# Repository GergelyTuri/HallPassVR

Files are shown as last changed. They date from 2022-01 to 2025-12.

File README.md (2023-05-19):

# HallPassVR
## Virtual reality system for head-fixed mouse experiments. 

See published paper on [JOVE](https://app.jove.com/v/64863/an-open-source-virtual-reality-system-for-the-measurement-of-spatial-learning-in-head-restrained-mice).

We developed an inexpensive, single board computer-based, easy-to-use setup for investigation of mouse spatial learning behavior using a visual virtual reality (VR) environment. This system uses a network of microcontrollers (ESP32) and a Raspberry Pi single-board computer to display a virtual linear track to a headfixed mouse running on a wheel. Along with a custom software package written in Python and C++ to generate parameterized virtual environments, this methodology allows researchers the design of various spatial navigation-based experiments to study neural circuits in the brain underlying spatial behaviors. [Example video here](https://www.youtube.com/watch?v=iCfhJT3dYIo):  

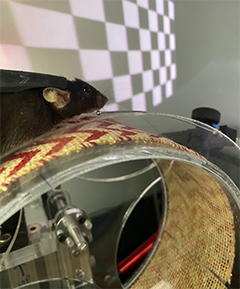
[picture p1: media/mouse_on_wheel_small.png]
Mouse on wheel


## Main hardware requirements: 
1. _ESP32 microcontrollers_ to track and convert mouse movement on a treadmill or wheel to serial data and to control other harware elements (lick spout for reward delivery).
2. _Raspberry Pi 4_ for building and simulating the virtual reality environment. 
3. _Projector_ for visualizing the virtual corridor.
4. PCB shields through [OpenMaze](https://claylacefield.wixsite.com/openmazehome/openmaze-shields)

## Software requirements: 
1. The virtual corridor was designed with _Python_. 
2. Native, Linux-based OS for Raspberry Pi.
3. _tkinter_ was used for designing the graphical user interface.
4. _Arduino IDE_ for programing the microcontrollers.
5. _Processing_ for data collection and plotting.
6. The analysis of behavior files currently requires _Matlab_.

### What we have done: 
1. We built the main part of the system which can simultaneously run and show the virtual reality environment on a computer display and a projector.
2. We have built a prototype GUI which can be used to build virtual corridors from virtually any kind of jpeg images.
3. We tested the system with several testbenches.

### Work in progress: 
1. Finalizing the code by adding documentation and examples.
                
### Future plans: 
1. Optimization of the system by e.g., adding an RFID sensor to increase wheel tracking accuracy.
3. Adding other features to the VR software like naturalistic scenes, looming stimulus or cliff-like effects. 
4. Implementing the analysis scripts in Python.
5. Increasing the flexibility of the existing protocols. 
6. Implementing a wireless (e.g., bluetooth) system using this platform.
## Quickstart:
### Initializing VR environment: 

1. Open a terminal window in Raspberry Pi and navigate to the `HallPassVR` folder
 ```bash
cd /home/pi/Documents/HallPassVR
 ```
2. Starting the VR GUI:
```bash
python3 HallPassVR_GUI.py
 ```
3. Setting up the floors and corridors in the GUI
4. Setting up `Processing` sketch to acquire and plot behavior.
5. Preliminary analysis of the acquired data can be done in Matlab with the scripts in `/Analysis code` folder.

#### GUI: 
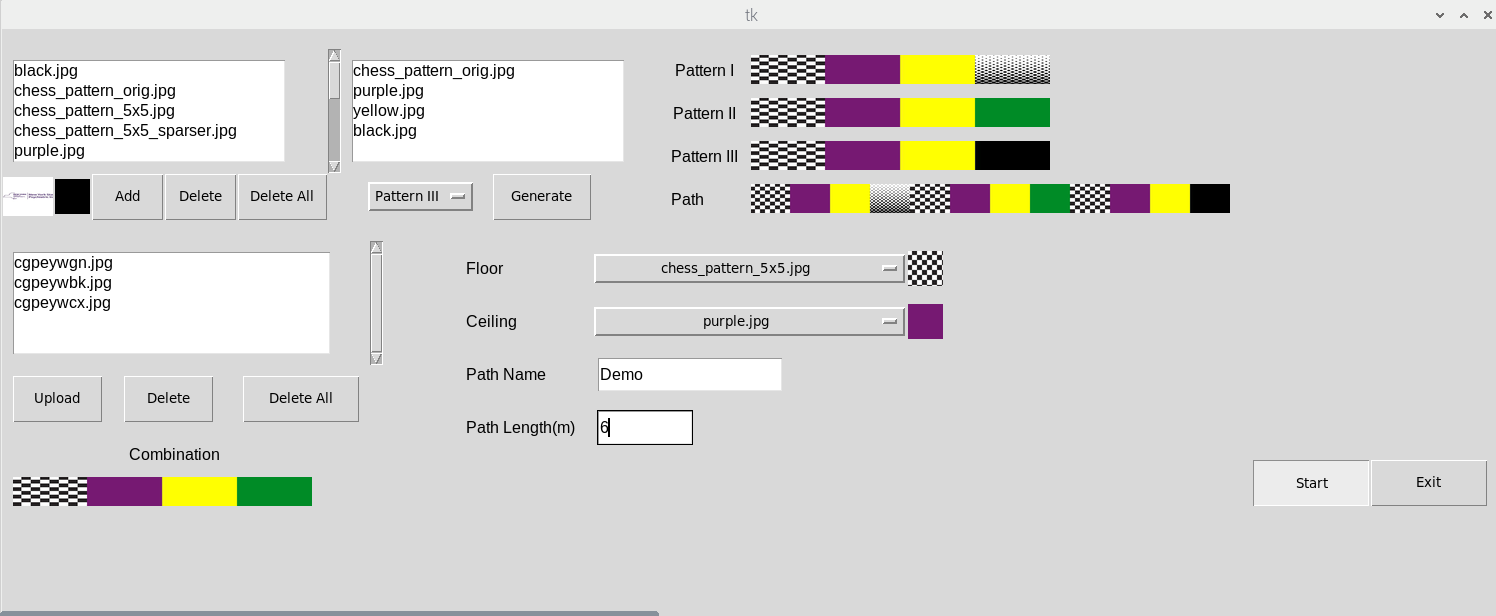
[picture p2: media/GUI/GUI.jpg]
GUI


#### Example virtual corridor: 
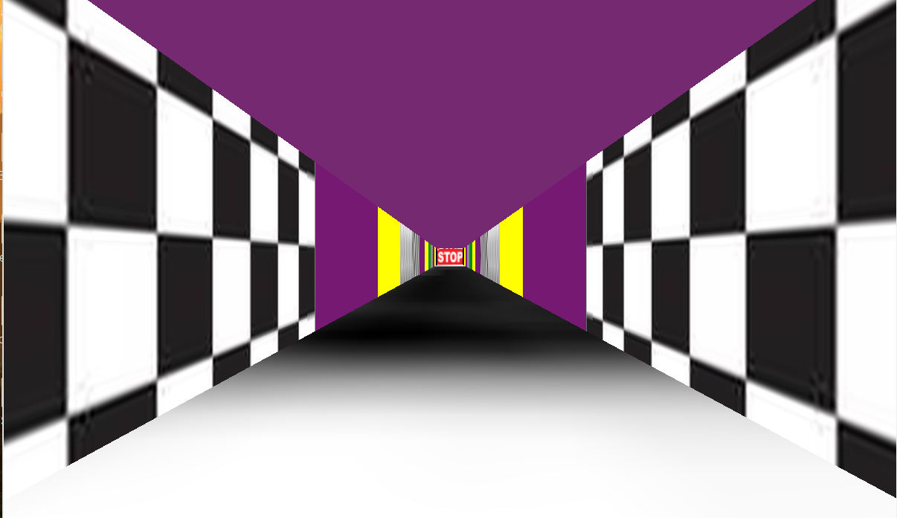
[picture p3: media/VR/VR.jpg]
corridor


For feature requests, support or questions, please open a ticket on [GitHub](https://github.com/GergelyTuri/mouseVR/issues).

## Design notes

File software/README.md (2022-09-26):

# HallPassVR software
## Virtual reality system for head-fixed mouse experiments. 

## Arduino code
1. Rotary encoder ESP32
2. Behavior ESP32 (with OMwESP32 PCB shield)

## Analysis code
MATLAB code for analysis of spatial licking behavior using .txt file output from Processing behavioral acquisition.

## Processing code
Code in the Processing.org environment to acquire data from behavior ESP32 during HallPassVR and plot relevant online behavioral events (and animal motion along the virtual linear track).

## HallPassVR Python code
To be copied onto RaspberryPi to run HallPassVR virtual linear track environment and GUI.

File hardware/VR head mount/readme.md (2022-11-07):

# This folder contains assembly files and instructions for the head mounting apparatus. 

Our headpost design consists of two interlocking manifolds for securing a metal headpost. We used a high resolution tabletop SLM 3D printer to manufacture the holding arms. The resin printed plastic is able to provide stable head fixation for behavior experiments, however, to achieve maximum stability for sensitive applications like single cell recording or two-photon imaging, we recommend using machined metal parts. The headpost holder is installed on two goniometers, with the tilting axes positioned perpendicular to each other, thus the animal’s head can be tilted to 4 directions after head fixation to level the preparation. The goniometers can represent a large price tag in this build, however, this feature is indispensable for chronic in vivo imaging experiments when finding the same cell population on subsequent imaging sessions is required. We deposited two types of head posts with different complexity (and price) we regularly use in our labs. Depending on the experiment type, the user should decide which one to implement. The head bars are made of steel (e.g., Stainless 304 Annealed) and we generally outsource the manufacturing of these parts to our local machine shop or to an online service (e.g., eMachineShop).

| material | description | source |
| -------- | ----------- | ------ |
| head post holder | custom 3D print | |
|set screws| M2.5 x 6 | McMasterr Carr|
|thumb screws|8-32 x 1/2"| McMasterr Carr|
|goniometers| Edmund Optics | 66-526, 66-527 |
| metal headposts | Stainless 304 Annealed or Titanium| [eMachineShop](https://www.emachineshop.com/)|
| optical posts (2) | 1/2" series| Thorlabs|
|right angle clamp| RA90| Thorlabs|

### Final look:
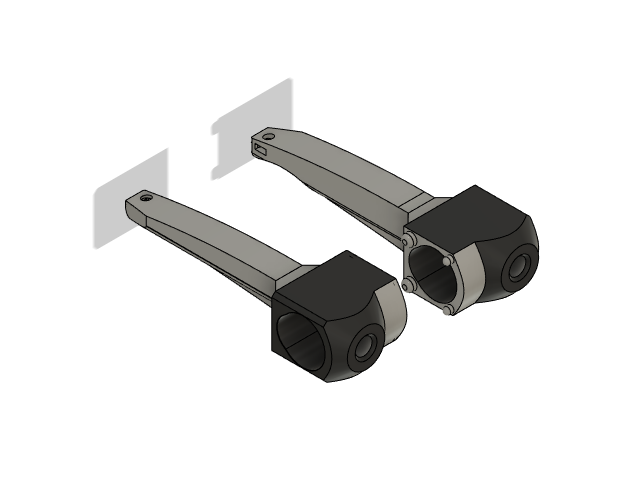
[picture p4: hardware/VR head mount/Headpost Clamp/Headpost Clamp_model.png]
clamp


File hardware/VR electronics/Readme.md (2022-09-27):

# Instructions for the electronic components

Files in the `ESP32 files` directory should be uploaded to the ESP32 boards connected to the lickport and rotary encoder. 

Files in `/PCBs` can get manufatured with companies specialized to PCB production. Typically we use [OSH Park](https://oshpark.com/) if we don't want to modify the design. More info on how to order and assemble these shields can be found on [OpenMaze](http://www.openmaze.org/).

| material | description | source |
| -------- | ----------- | ------ |
| Raspberry Pi 4 model B | single-board computer | e.g., raspberrypi.com, adafruit.com |
| rotary encoder | ENS1J-B28-L00256L | digikey.com[^1] |
|ESP32 devKitC v4 | microcontroller (x2)| e.g., [Amazon.com](https://www.amazon.com/s?k=ESP32&crid=ZCZ3J597DJO9&sprefix=esp32%2Caps%2C94&ref=nb_sb_noss_1)|
|OpenMaze OMwESP32 shield| custom design | see: `/PCBs` folder |

[^1]: Alternative sources: amazon.com, mouser.com, DigiPart, etc.

## Installation instructions for Raspberry Pi:
### Configure RaspberryPi 4 model B 
This single-board computer has an onboard GPU to facilitate VR environment rendering, as well as two HDMI ports for experiment control/monitoring and VR projection.
1. Download Raspberry Pi Imager app and install OS (currently RaspberryPi OS r.2021-05-07) on microSD card (8GB+), insert and boot Raspberry Pi.
2. Configure Raspberry Pi: (menu bar) 
- `Preferences>Raspberry Pi Configuration>`
  - `Display>Screen Blanking>Disable`
  - `Interfaces>Serial Port>Enable` 
  - `Performance>GPU Memory>256`
3. In the terminal: 
``` bash
sudo nano /boot/config.txt
``` 
then uncomment `config_hdmi_boost=4`. Save, reboot the Raspberry Pi.

4. Download and install Arduino IDE from arduino.cc/en/software (e.g. arduino-1.8.19-linuxarm.tar.gz)
5. Download and install Processing IDE from github.com/processing/processing4/releases (e.g. processing-4.0.1-linux-arm32.tgz)
6. In the terminal
```bash
sudo pip3 install pillow –-upgrade
```
7. Then, 
```bash
sudo pip3 install pi3d
```
8. Install ESP32 support on Arduino IDE.

## Set up rotary encoder-ESP32 connections
1. Connect wires between rotary encoder and ESP32.
2. Connect serial RX/TX wires between ESP32 Serial2 (pins 16,17) and behavior ESP32.
3. Connect serial RX/TX wires between ESP32 Serial0 (RX/TX) and Raspberry Pi GPIO (or direct USB connection).
4. Set up behavior ESP32 connections with behavioral hardware (via OMwESP32small PCB).
5. Connect 12V liquid solenoid valve to ULN2803 IC output (e.g. pin#32).
6. Connect lick port to ESP32 touch inputs (e.g. T2, GPIO15).
7. Connect serial RX/TX wires between behav ESP32 Serial2 (pins 16,17) and rotary encoder ESP32 (see above #1.b.).
8. Plug USB into Raspberry Pi USB port (or other PC running Processing to capture behavior data).
9. Plug Raspberry Pi HDMI #2 output into projector HDMI port.

## Set up software (rotary encoder ESP32 and behavior ESP32 w. OM PCB)
1. Plug rotary encoder ESP32 into Raspberry Pi USB port first- it will be automatically be named `/dev/ttyUSB0`
2. Load rotary encoder arduino code by first selecting the ESP32 under `Arduino IDE>Tools>Boards>ESP32 Dev Module`, then `Tools>Port`>`/dev/ttyUSB0`, then click `Upload`: `RotaryEncoder_Esp32_VR.ino`
3. Plug behavior ESP32 into Raspberry Pi USB port next- it will be named `/dev/ttyUSB1`
4. Load behavior sequence arduino code (ESP32 Dev Module already selected), then `Tools>Port>` `/dev/ttyUSB1`, then click `Upload`: `wheel_VR_behavior.ino`
5. You can test serial connections by selecting the Port in the Arduino IDE, then clicking on `Tools>Serial Monitor` (baud rate:115200), to observe serial output from the rotary board (USB0) or the behavior board (USB1).
6. Download HallPassVR python code from this GitHub repo (`/software/HallPassVR`) to `/home/pi/Documents`.

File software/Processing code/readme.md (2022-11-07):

# HallPassVR
## Virtual reality system for head-fixed mouse experiments. 

Processing code to record and graph serial data from behavior ESP32 (w. HallPassVR).

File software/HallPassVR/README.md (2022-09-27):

# HallPassVR
## Virtual reality system for head-fixed mouse experiments. 

To be copied onto RaspberryPi to run HallPassVR virtual linear track environment and GUI.

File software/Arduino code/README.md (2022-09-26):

# HallPassVR
## Virtual reality system for head-fixed mouse experiments. 

Code written for Arduino IDE to run rotary encoder ESP32 and behavior ESP32 with OpenMaze OMwESP32 PCB.

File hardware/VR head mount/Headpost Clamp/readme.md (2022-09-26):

### This folder contains assembly files and instructions for the headpost holder. 

#### Design:

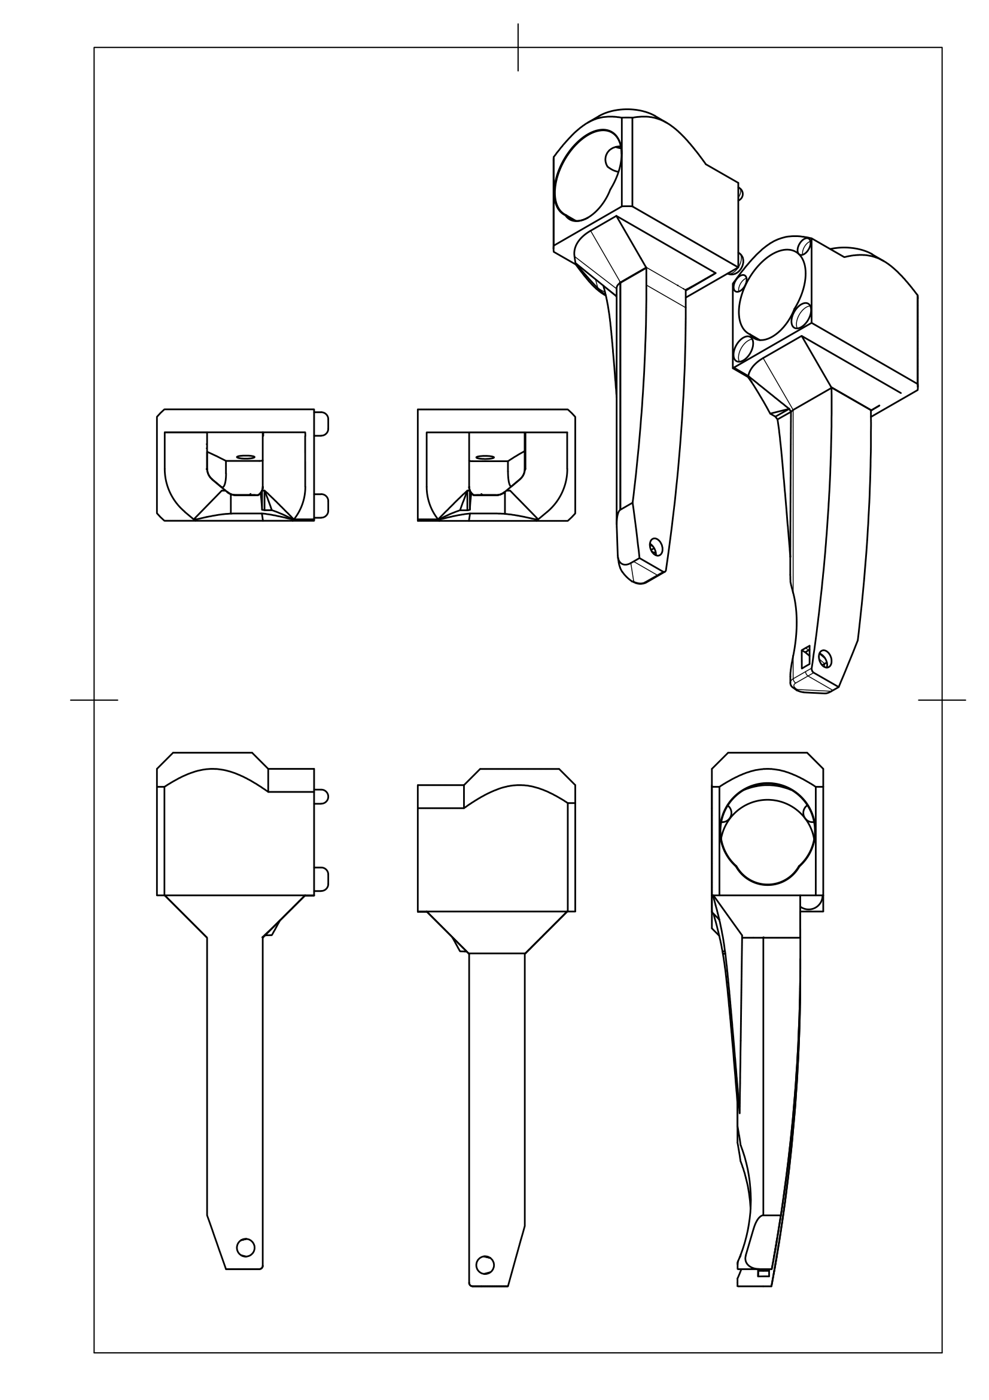
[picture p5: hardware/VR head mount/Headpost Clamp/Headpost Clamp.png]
clamp


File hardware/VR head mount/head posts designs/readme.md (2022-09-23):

### This folder contains assembly files and instructions for the headposts. 

We use an online service to have the headposts manufactured. Typically we use annealed 304 stainless steal as material. If weigth is a concern then using titanium can be considered.

#### Design:
 see pdf files.

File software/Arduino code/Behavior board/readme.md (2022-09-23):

code for behavior board comes here. i beleive currently it is in the `/VR electronics` folder

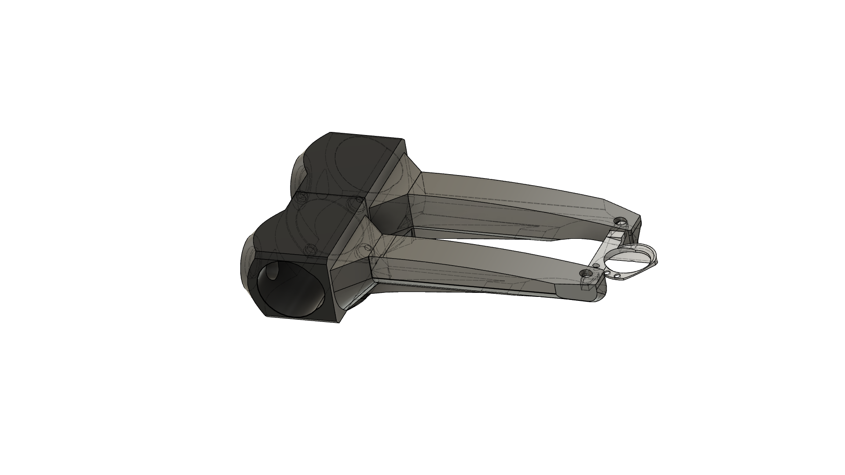
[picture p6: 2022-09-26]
hardware/VR head mount/Headpost Clamp/Headpost and Clamp.png

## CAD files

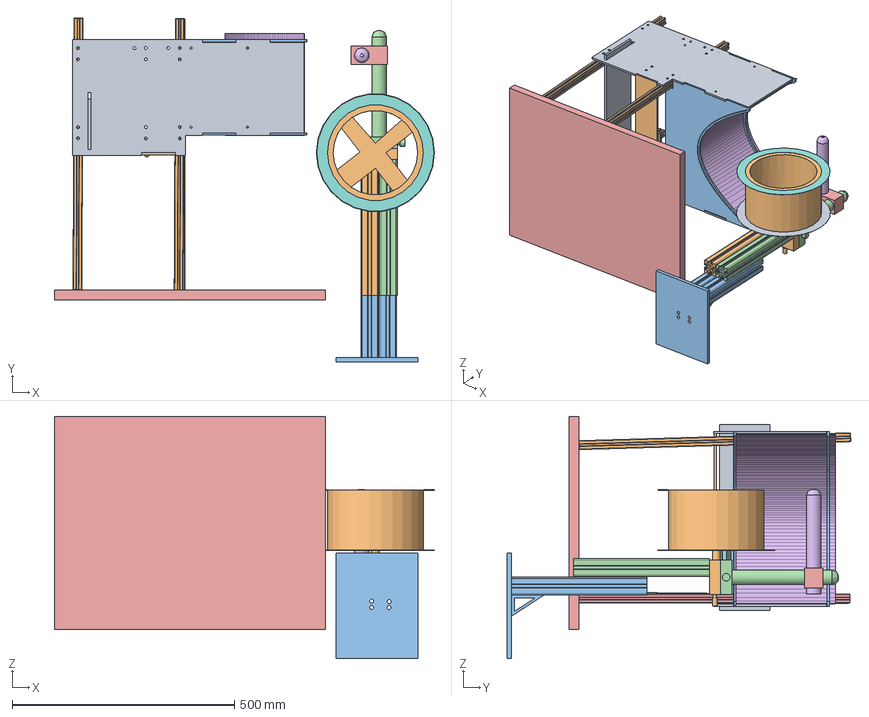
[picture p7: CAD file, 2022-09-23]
media/screen/Screen and Wheel Assemblies.step
854.4 x 772.9 x 544.8 mm
5537T709_T-Slotted Framing
5537T104_T-Slotted Framing

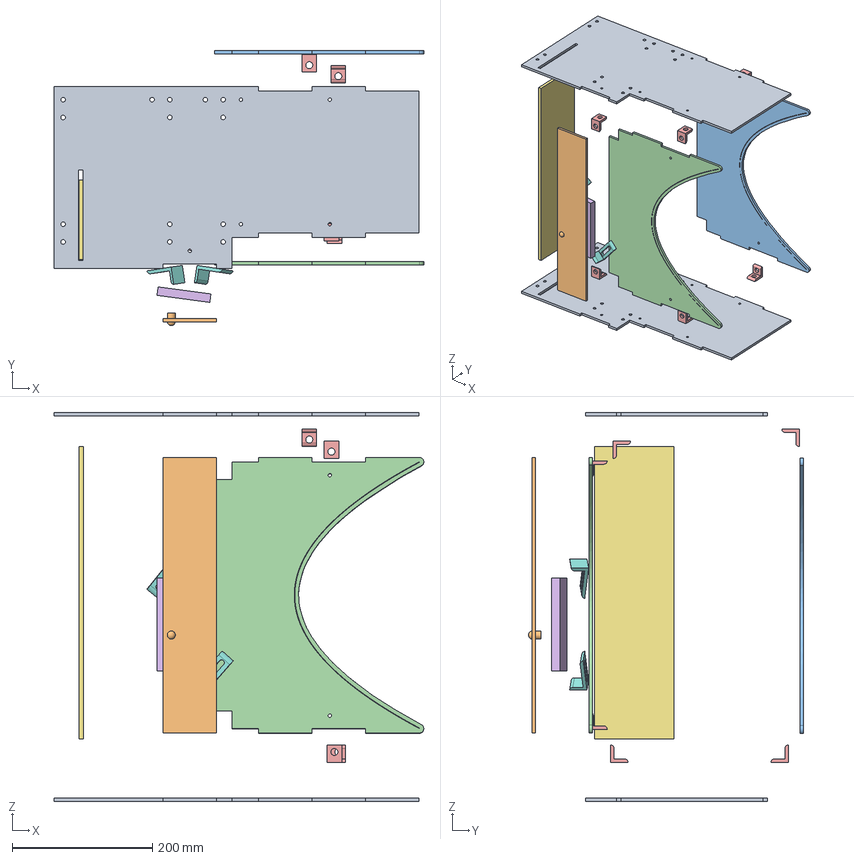
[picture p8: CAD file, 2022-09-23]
hardware/VR screen assembly/Screen Assemblies.step
527.9 x 392.9 x 555.6 mm
Right
Left
Stand1
Top
Bottom
Corner Bracket x 2
Stand2
Mirror
Top Bracket 1
Top Bracket 2
Bottom Bracket 1
Bottom Bracket 2
L Bracket 1 x 2

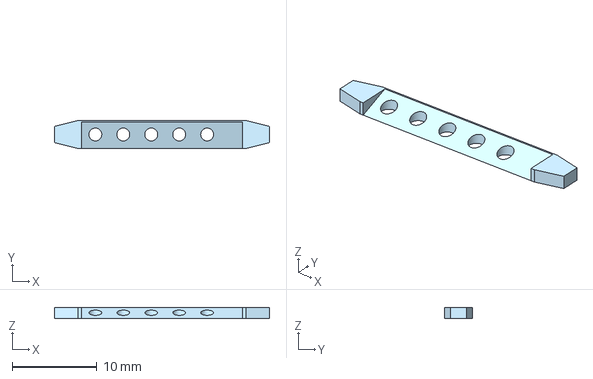
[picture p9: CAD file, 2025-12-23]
hardware/VR head mount/head posts designs/straight post0.step
25.4 x 3.30 x 1.27 mm

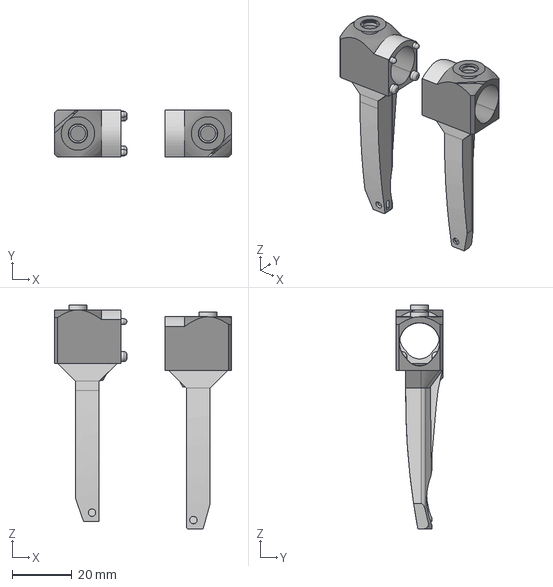
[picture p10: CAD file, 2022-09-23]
hardware/VR head mount/Headpost Clamp/Headpost Clamp.step
59.2 x 15.8 x 75.5 mm
Left v2
Right v2

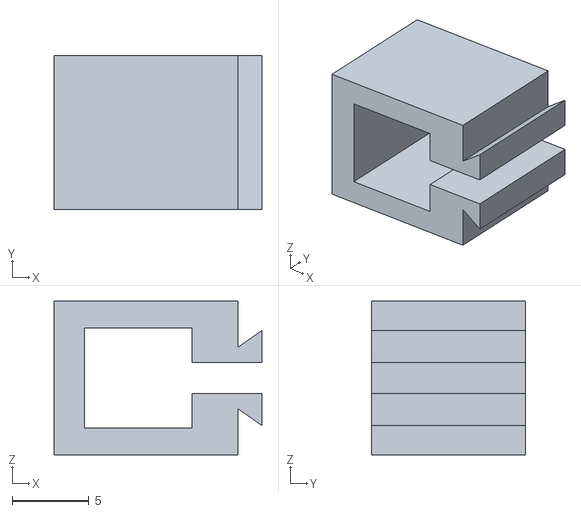
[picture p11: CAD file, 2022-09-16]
hardware/VR lickport assembly/water spout holder for 16 needle.stl
13.6 x 10.0 x 10.0

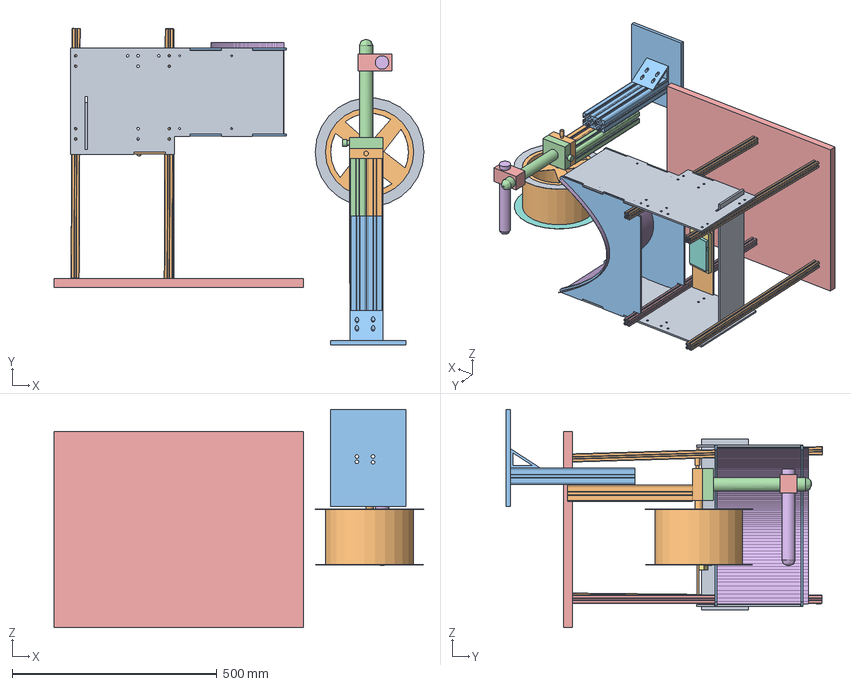
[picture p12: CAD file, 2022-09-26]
hardware/VR screen assembly/Wheel and Sceen.step
903.5 x 772.9 x 532.7 mm
5537T709_T-Slotted Framing
5537T104_T-Slotted Framing

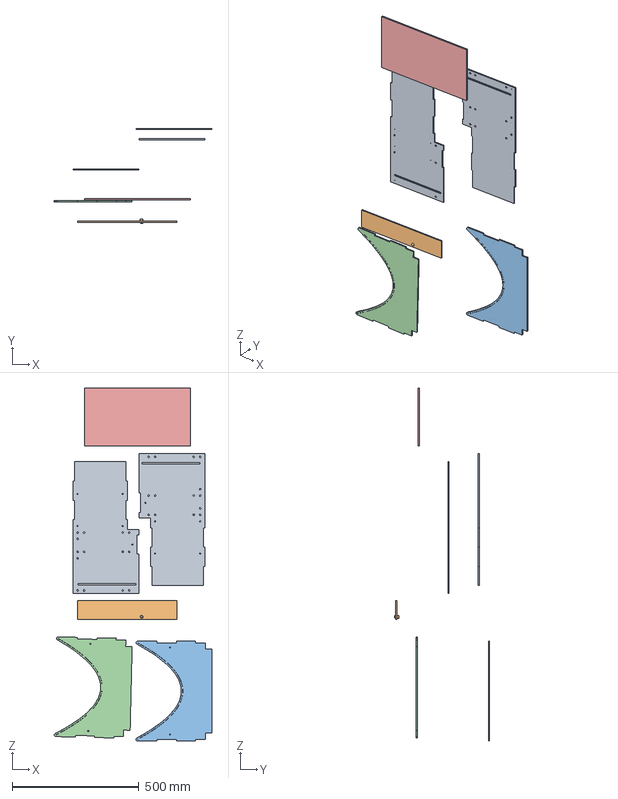
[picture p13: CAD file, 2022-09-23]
hardware/VR screen assembly/Laser Cut Part.step
621.7 x 376.7 x 1392.3 mm
Right
Left
Stand1
Top
Bottom

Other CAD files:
hardware/VR wheel assembly/runningWheel_6inCyl_sideMount_JoVE_091422a.dxf
hardware/VR head mount/head posts designs/straight headpost.step
hardware/VR head mount/head posts designs/straightHeadpostTemplate_100416h.dwg
hardware/VR head mount/head posts designs/headppost_Turi_2gen_FINAL.ipt

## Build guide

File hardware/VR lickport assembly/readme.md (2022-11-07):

# Instructions for assembling the lickport

We developed a capacitive touch sensor lick port which is highly sensitive and easy to implement. A metal water spout is connected to ESP32 board which detects lick touch events and delivers liquid rewards via a solenoid valve actuated by an H-bridge circuit on the OpenMaze OMesp32 PCB. The sensitivity of the port can be tuned. Note: this type of lick sensor can introduce a significant amount of electric noise when the mouse licks the spout which could be disadvantageous for electrophysiological recordings. Please contact the authors for alternative solutions using IR beam break lick detection. 

| material | description | source |
| -------- | ----------- | ------ | 
|ESP32 | microcontroller | e.g., [Amazon.com](https://www.amazon.com/s?k=ESP32&crid=ZCZ3J597DJO9&sprefix=esp32%2Caps%2C94&ref=nb_sb_noss_1)|
|ESP32 shield| custom design | OpenMaze.org |
|Capacitive Touch Breakout|AT42QT1010|Sparkfun|
| lick spout | 20068-638[^1]| [VWR](https://us.vwr.com/store/) |
|adjustable arm| for holding the lick spout | [Amazon](https://www.amazon.com/Magnetic-Adjustable-Indicator-Holder-Digital/dp/B00L5T2ZA8) |
|arm holder| 3D printed| attach file @claylacefield|
|spout holder| 3D printed | `water spout holder for 16 needle.stl` |
|solenoid valve |003-0137-900 | [Parker]([003-0137-900](https://ph.parker.com/us/12051/en/series-3-miniature-inert-liquid-valve/003-0137-900))|
|tubing and water reservoir | for delivering water| e.g., [this](https://www.fishersci.com/shop/products/exel-international-iv-administration-set-2/p-2624960)|

[^1]: Any other (metal) spout works. 
### Final assembly:

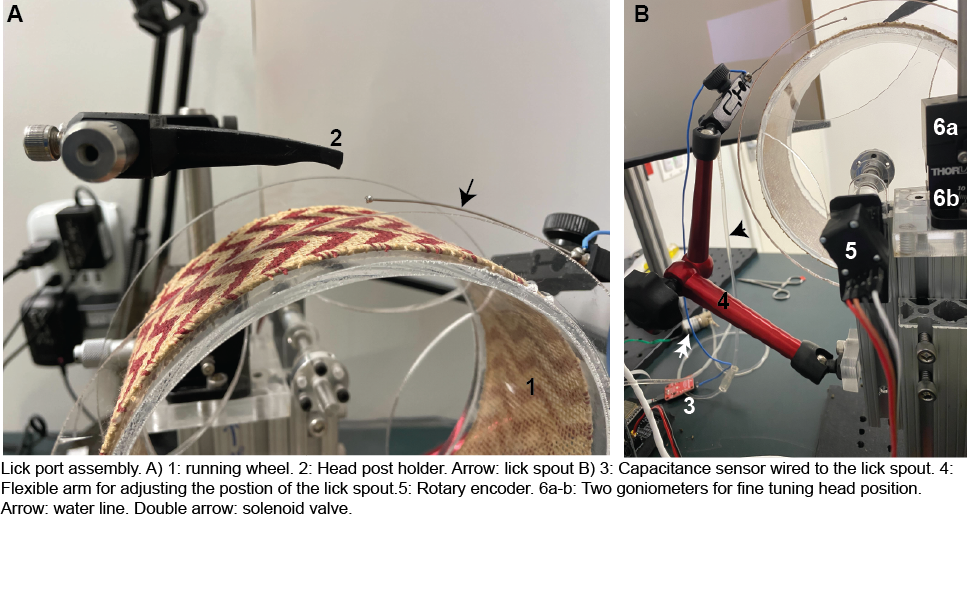
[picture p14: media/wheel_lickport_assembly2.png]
Lickport


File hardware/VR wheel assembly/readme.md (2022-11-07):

# Instructions and files for assembling the runinng wheel.

We use 1/4" thick, clear acrylic to cut out the wheel parts found in `runningWheel_6inCyl_sideMount_JoVE_091422a.ai`.

## Bill of Materials

| material | description | source |
| -------- | ----------- | ------ |
| acrylic sheet, laser cutting template[^1]  | 1/4" thick | e.g., Canalplastic: 32920770574|
| acrylic cylinder | 6" diam, 3" thick | e.g., Canalplastic: 33210090702|
|SCIGRIP 10315 acrylic cement|gluing the parts|e.g., [this](https://www.amazon.com/SCIGRIP-10315-Acrylic-Cement-Low-VOC/dp/B003HNFLMY)|
| ball bearing (2x)| 5/8" OD, 1/4" ID | McMasterr Carr: 57155K324|
| T-slotted aluminum extrusion [^2] | 2 x 7" | 8020.net |
|fasteners and brackets|4138, 3382, 3280|8020.net|
| axle | 1/4" diam, 3" long | McMasterr Carr: 9062K26|
| optical breadboard | base, as per user's requirements | Throlabs|
|shaft coupler|coupling the axis to the rotary encoder| [McMaster-Carr](https://www.mcmaster.com/shaft-couplings/set-screw-precision-flexible-shaft-couplings/for-shaft-misalignment-type~axial/system-of-measurement~inch/for-shaft-diameter~1-4/length~3-4-2/):9861T426|
|axle mounting flange, 1/4" ID|keeping the axis in the center of the wheel|Pololu: 1993|

#### Wheel laser cutting template:
[^1]: The same template is atteched here with .ai, .dxf and .svg extensions. 
[^2]: We used 1020 (dual) style extrusion profiles for this build for increased stability. Fasteners and brackets can also be sourced from 8020.net 

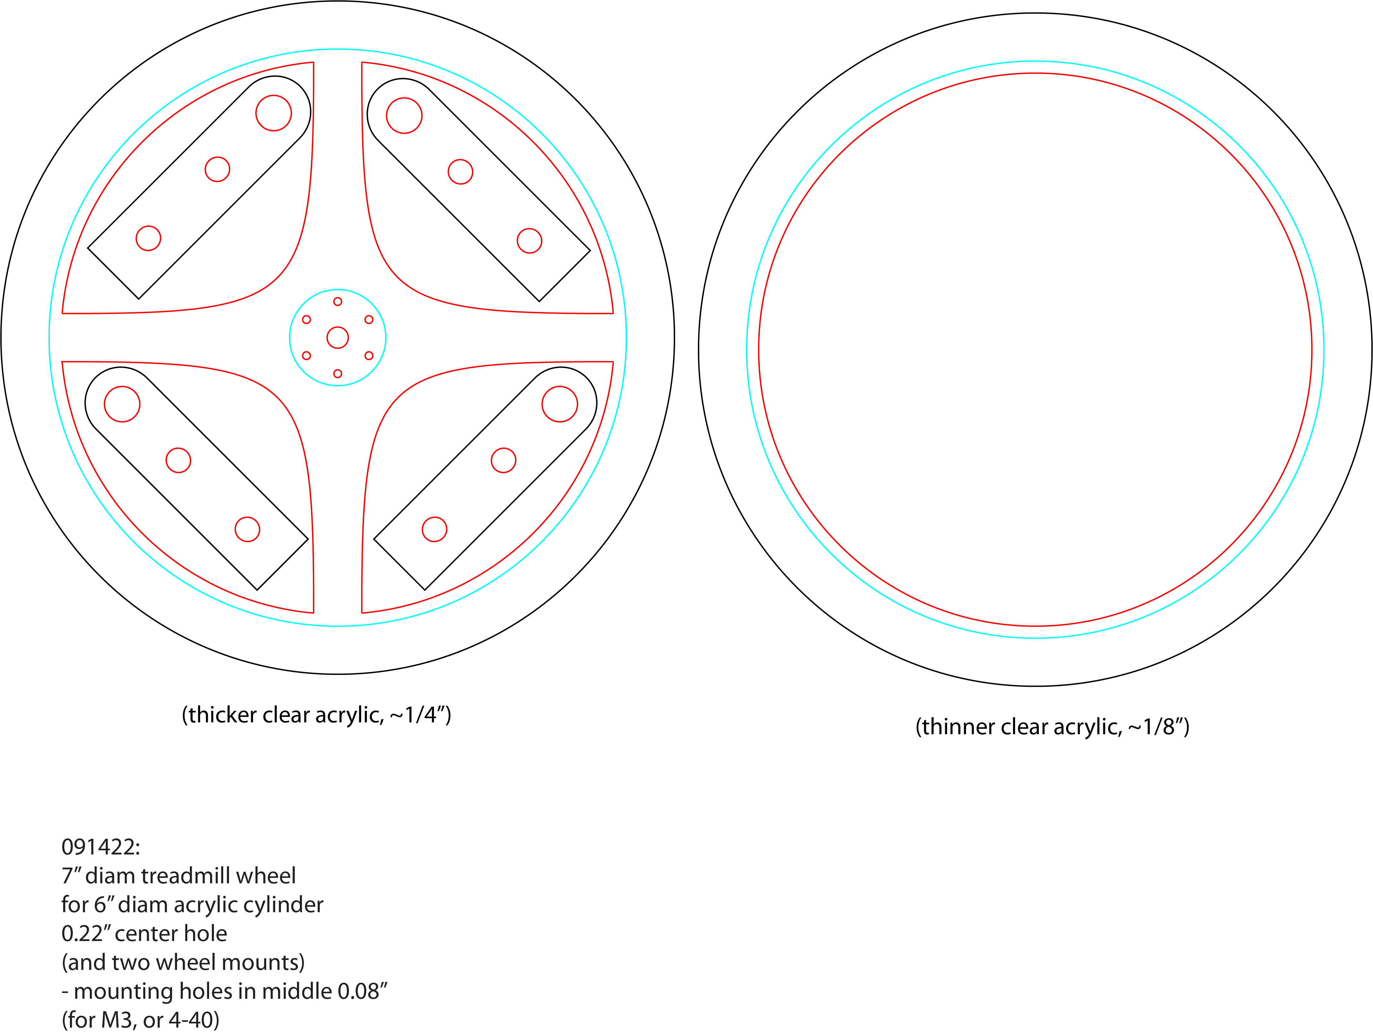
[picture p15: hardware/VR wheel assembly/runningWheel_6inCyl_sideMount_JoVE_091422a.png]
wheel


#### Final Assembly
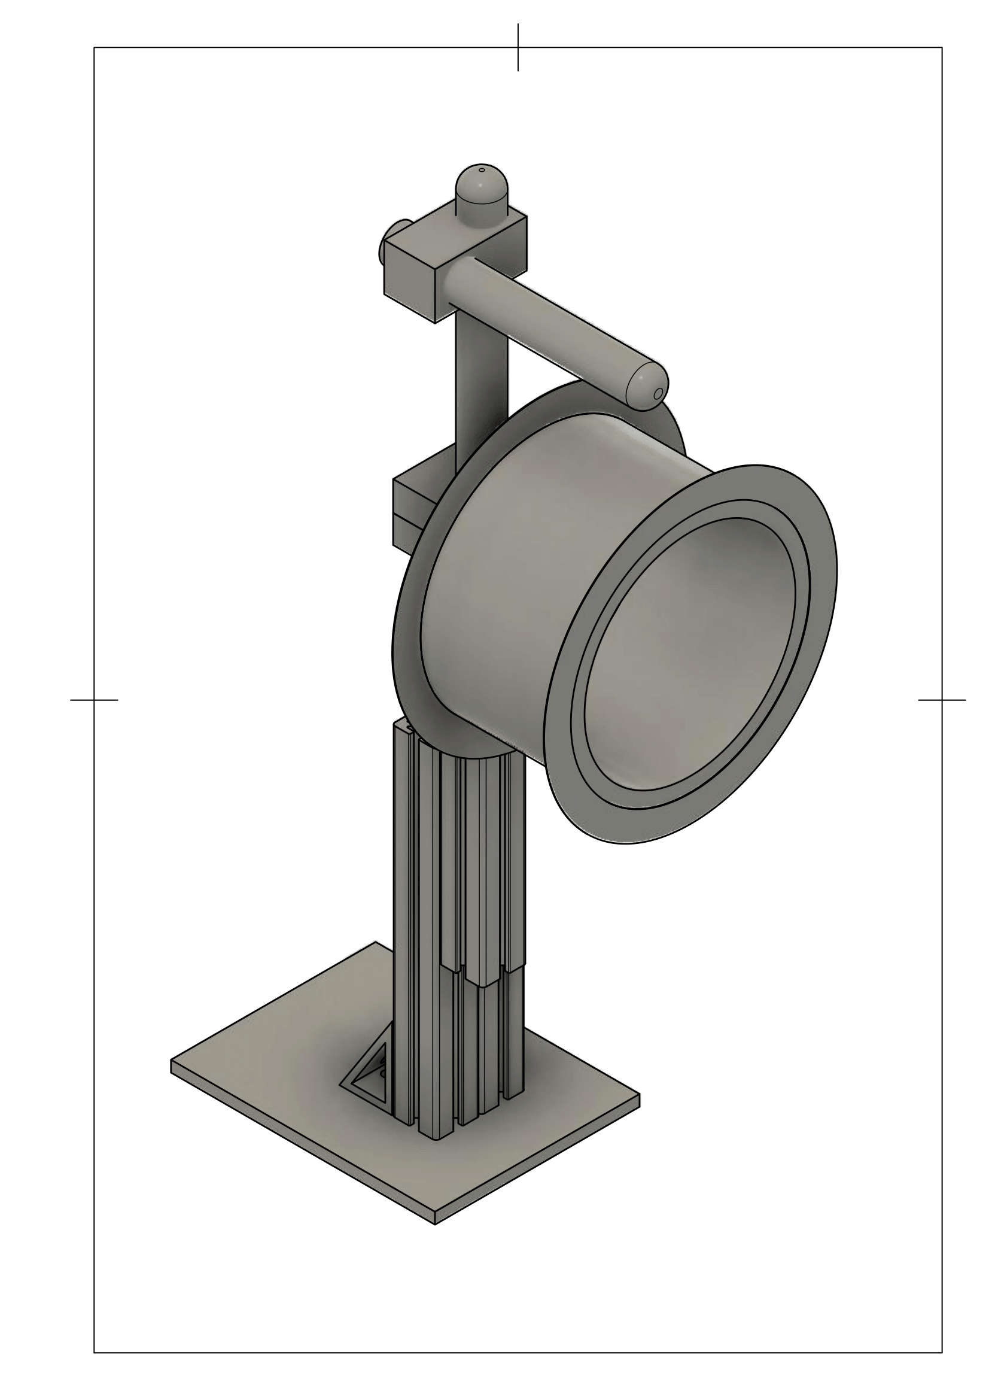
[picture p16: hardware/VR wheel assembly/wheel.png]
wheel


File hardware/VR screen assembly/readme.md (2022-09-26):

# Instructions and files for building the screen.

The design is based on the screen developed in [Chris Harvey's lab](https://github.com/HarveyLab/mouseVR). It is highly recommended to read that documentation along with ours to tailor the VR environment to the user’s needs. Since the laser projector in the original description is not available any more, we used a LED projector from Texas Instrument. The projection angle (keystone) is different from that of a laser projector we, we slightly modified the design by mounting the device underneath the screen and simplifying the mirror system. 

## Bill of materials

| material | description | source |
| -------- | ----------- | ------ |
| DLP® LightCrafter™ Display 2010 Evaluation Module [^1] | DLPDLCR2010EVM |Texas Instrument |
|front surface mirror|114 mm x 418 mm|[first surface mirror](https://firstsurfacemirror.com/)|
|Silver Mirror Acrylic Sheet [^2] | cheap alternative| e.g., [Canal Plastics Center](https://www.canalplastic.com/) |
|plastic sheets| as per the design files| e.g., [Canal Plastic Center](https://www.canalplastic.com/)|
|24" x 48" Matte white diffusion paper|screen material|e.g., [this](https://www.bhphotovideo.com/c/product/44042-REG/Rosco_RS302611_3026_Filter_Tough.html)| 

[^1]: at the time of the writing, this module was unavailable at TI's website. We probably recommend DLPDLCR230NPEVM.
[^2]: Crispier image qulaity can be achieved by investing in a more expensive [front surface mirror](https://firstsurfacemirror.com/) 

### Assembling instructions:
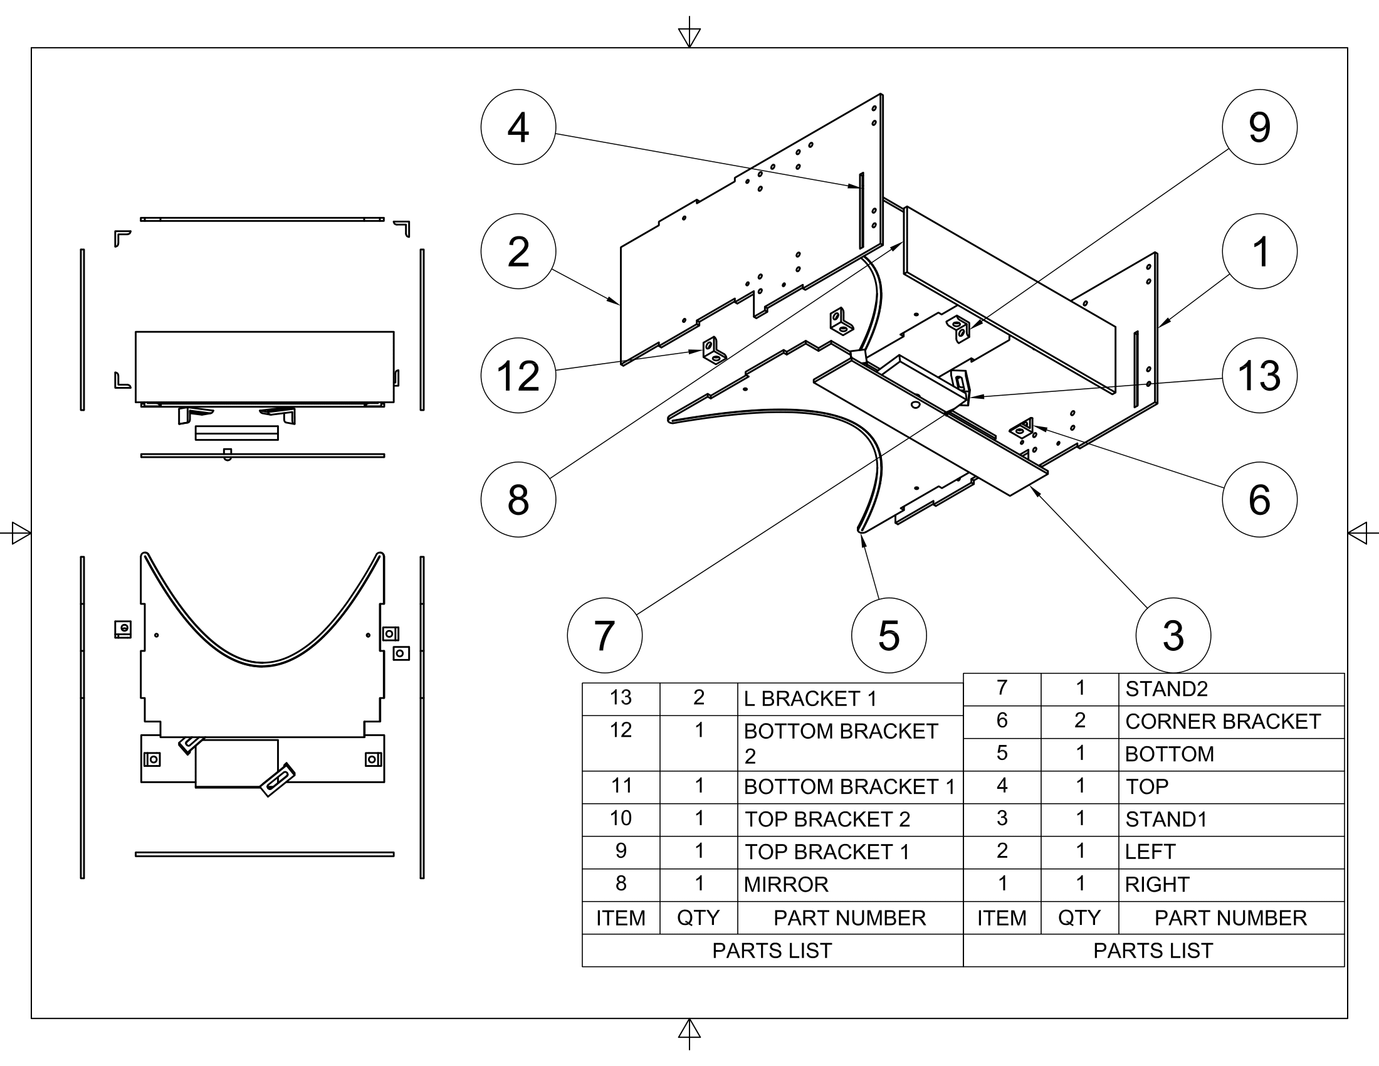
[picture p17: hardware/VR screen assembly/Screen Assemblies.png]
Screen


### Final look:
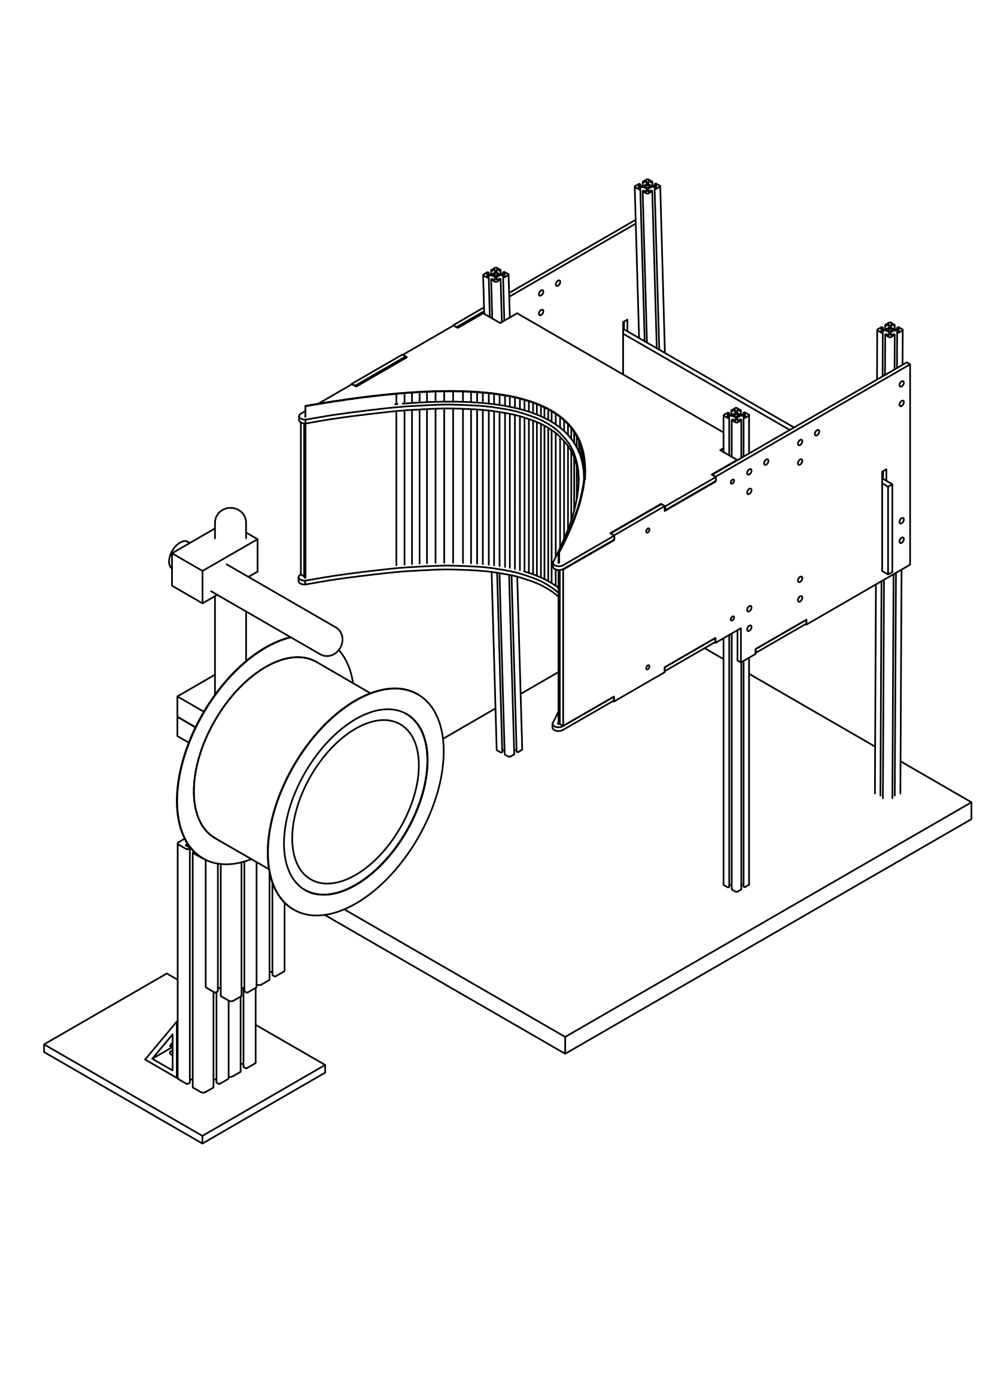
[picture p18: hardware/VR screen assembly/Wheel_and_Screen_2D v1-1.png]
Screen


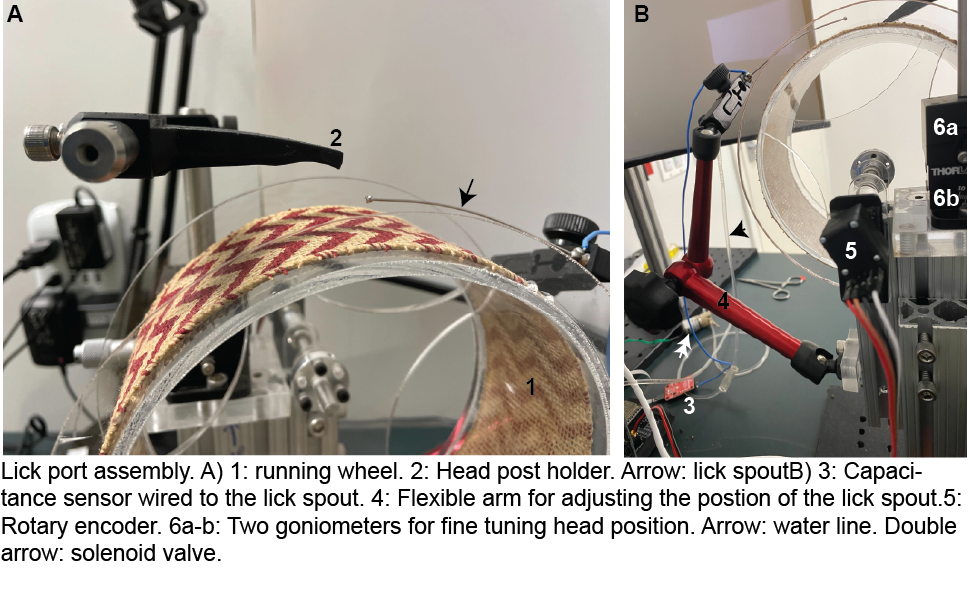
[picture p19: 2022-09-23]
media/wheel_lickport_assembly.png

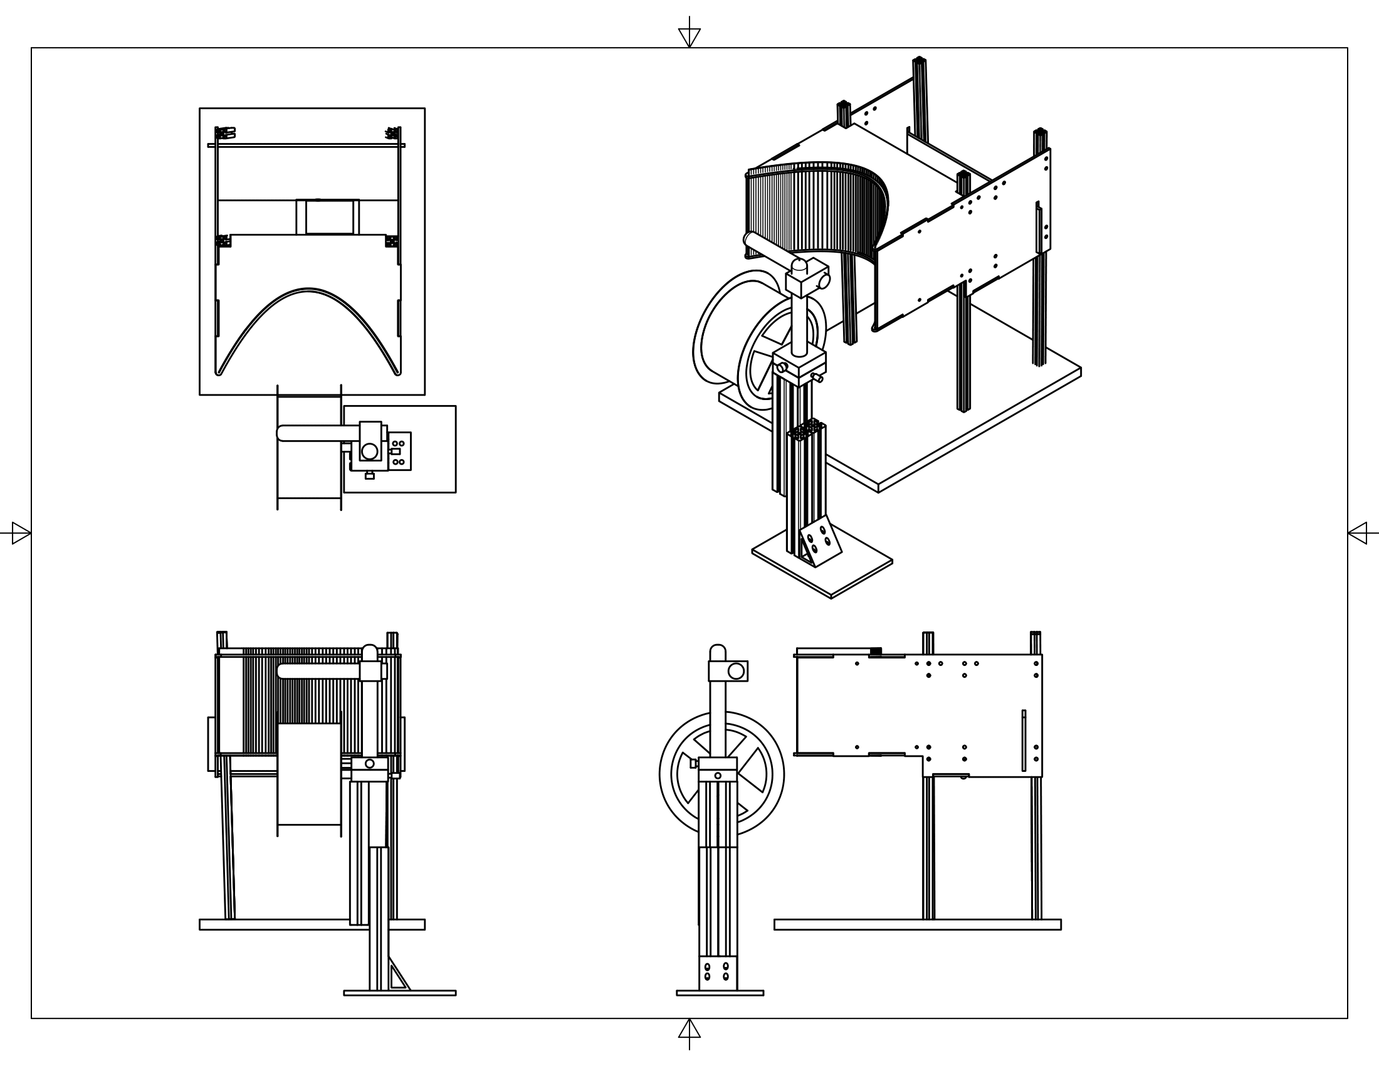
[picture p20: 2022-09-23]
media/screen/Screen and Wheel Assemblies.png

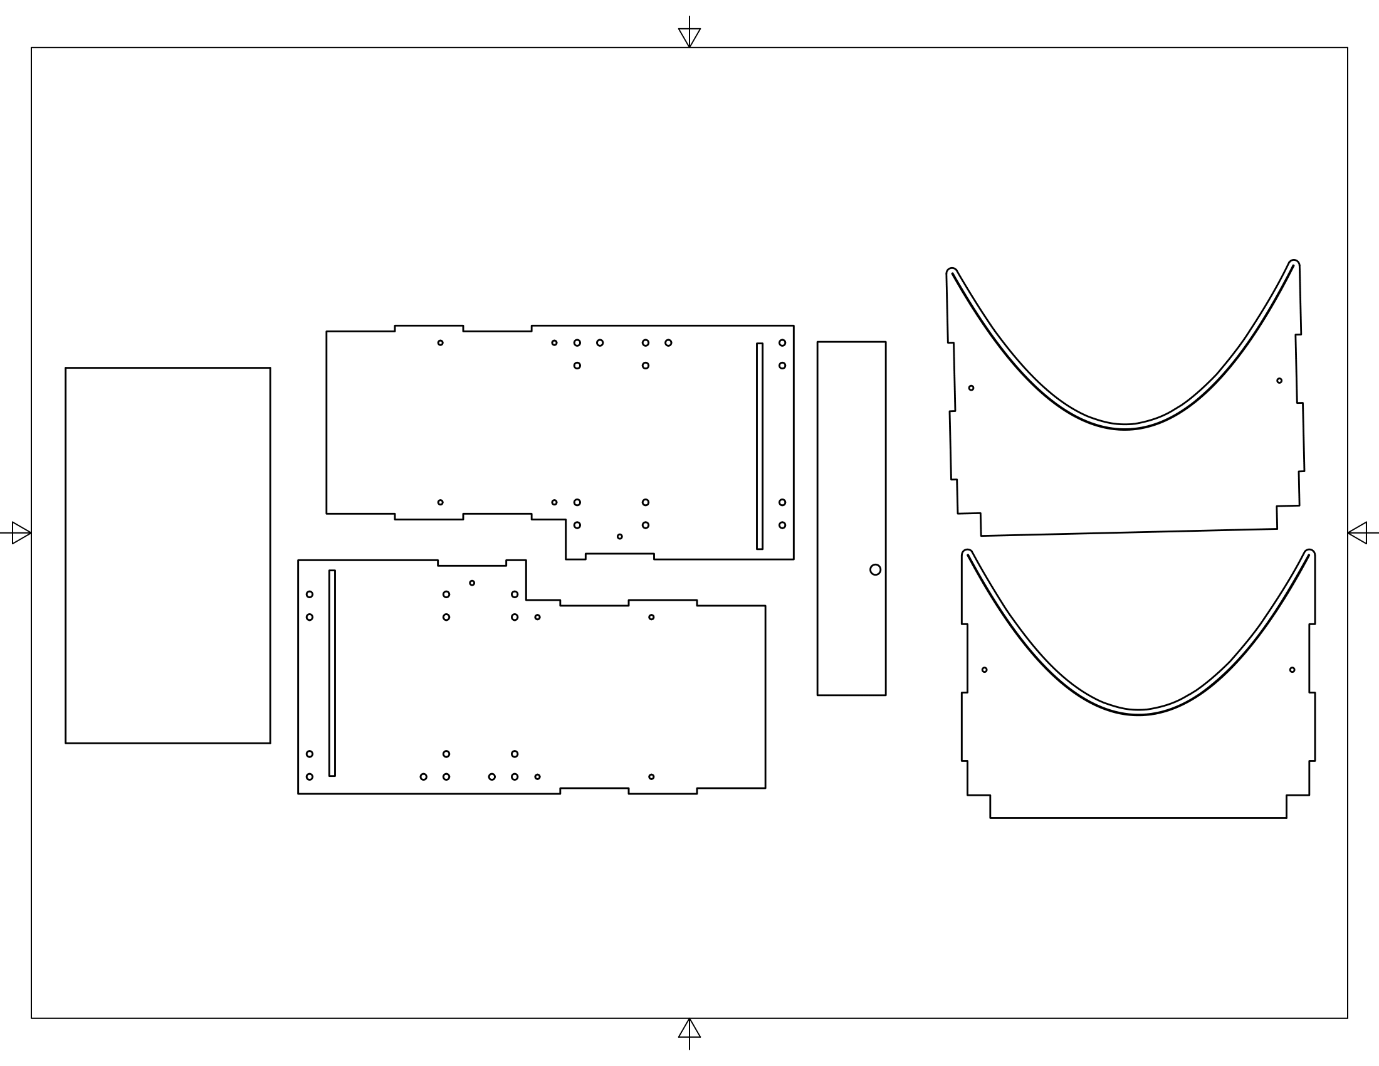
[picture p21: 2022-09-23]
hardware/VR screen assembly/Laser Cut Part.png

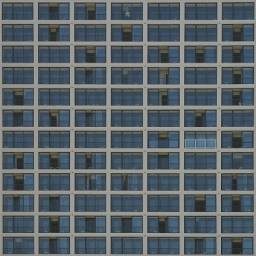
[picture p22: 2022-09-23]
software/HallPassVR/textures/glassbuilding.jpg

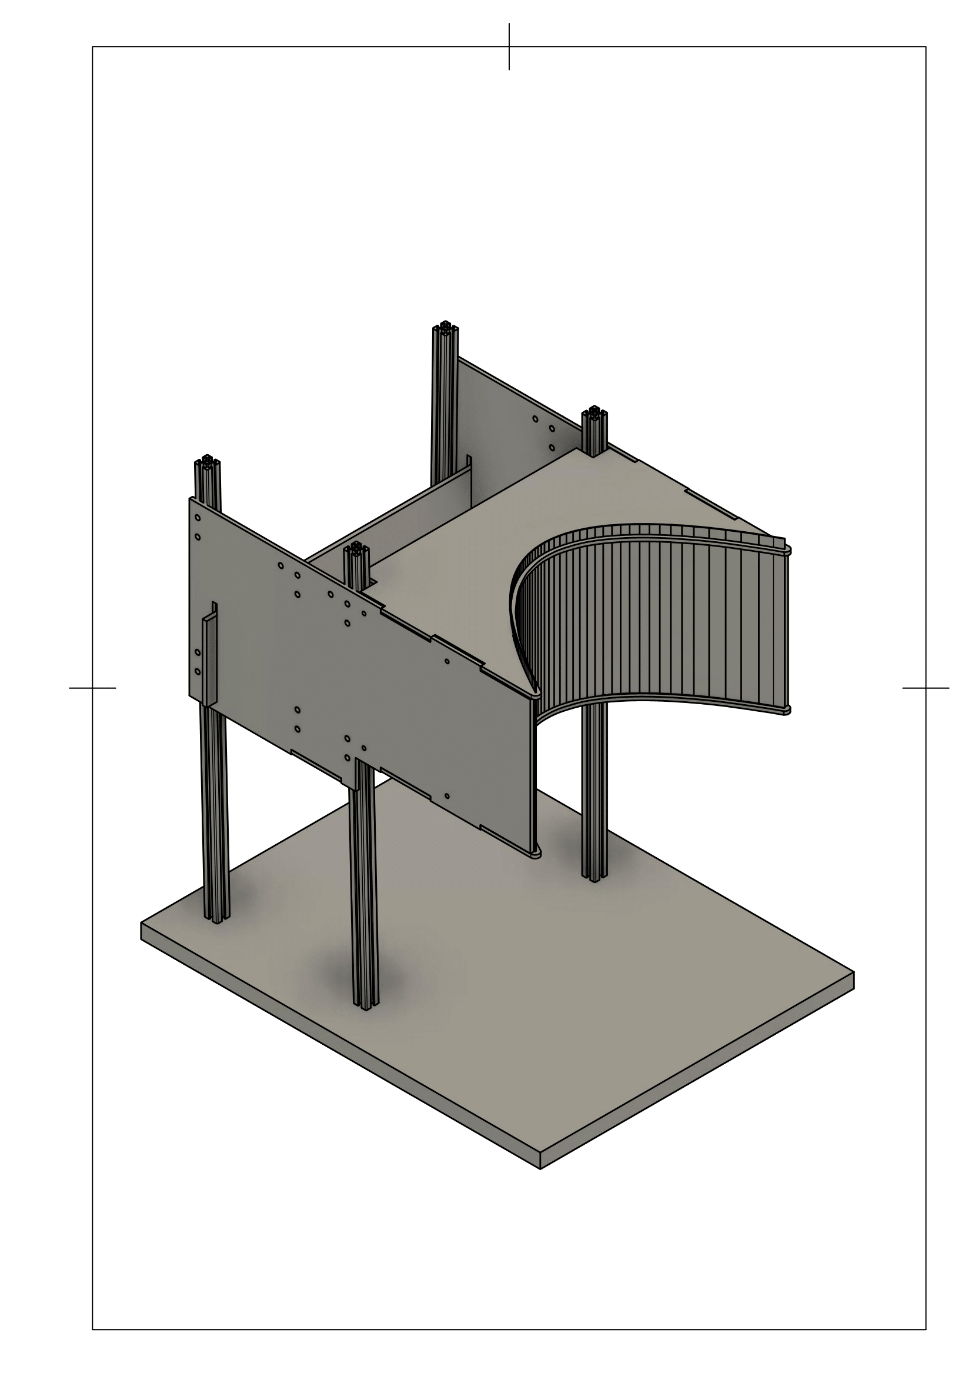
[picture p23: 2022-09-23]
hardware/VR screen assembly/Screen Image.png

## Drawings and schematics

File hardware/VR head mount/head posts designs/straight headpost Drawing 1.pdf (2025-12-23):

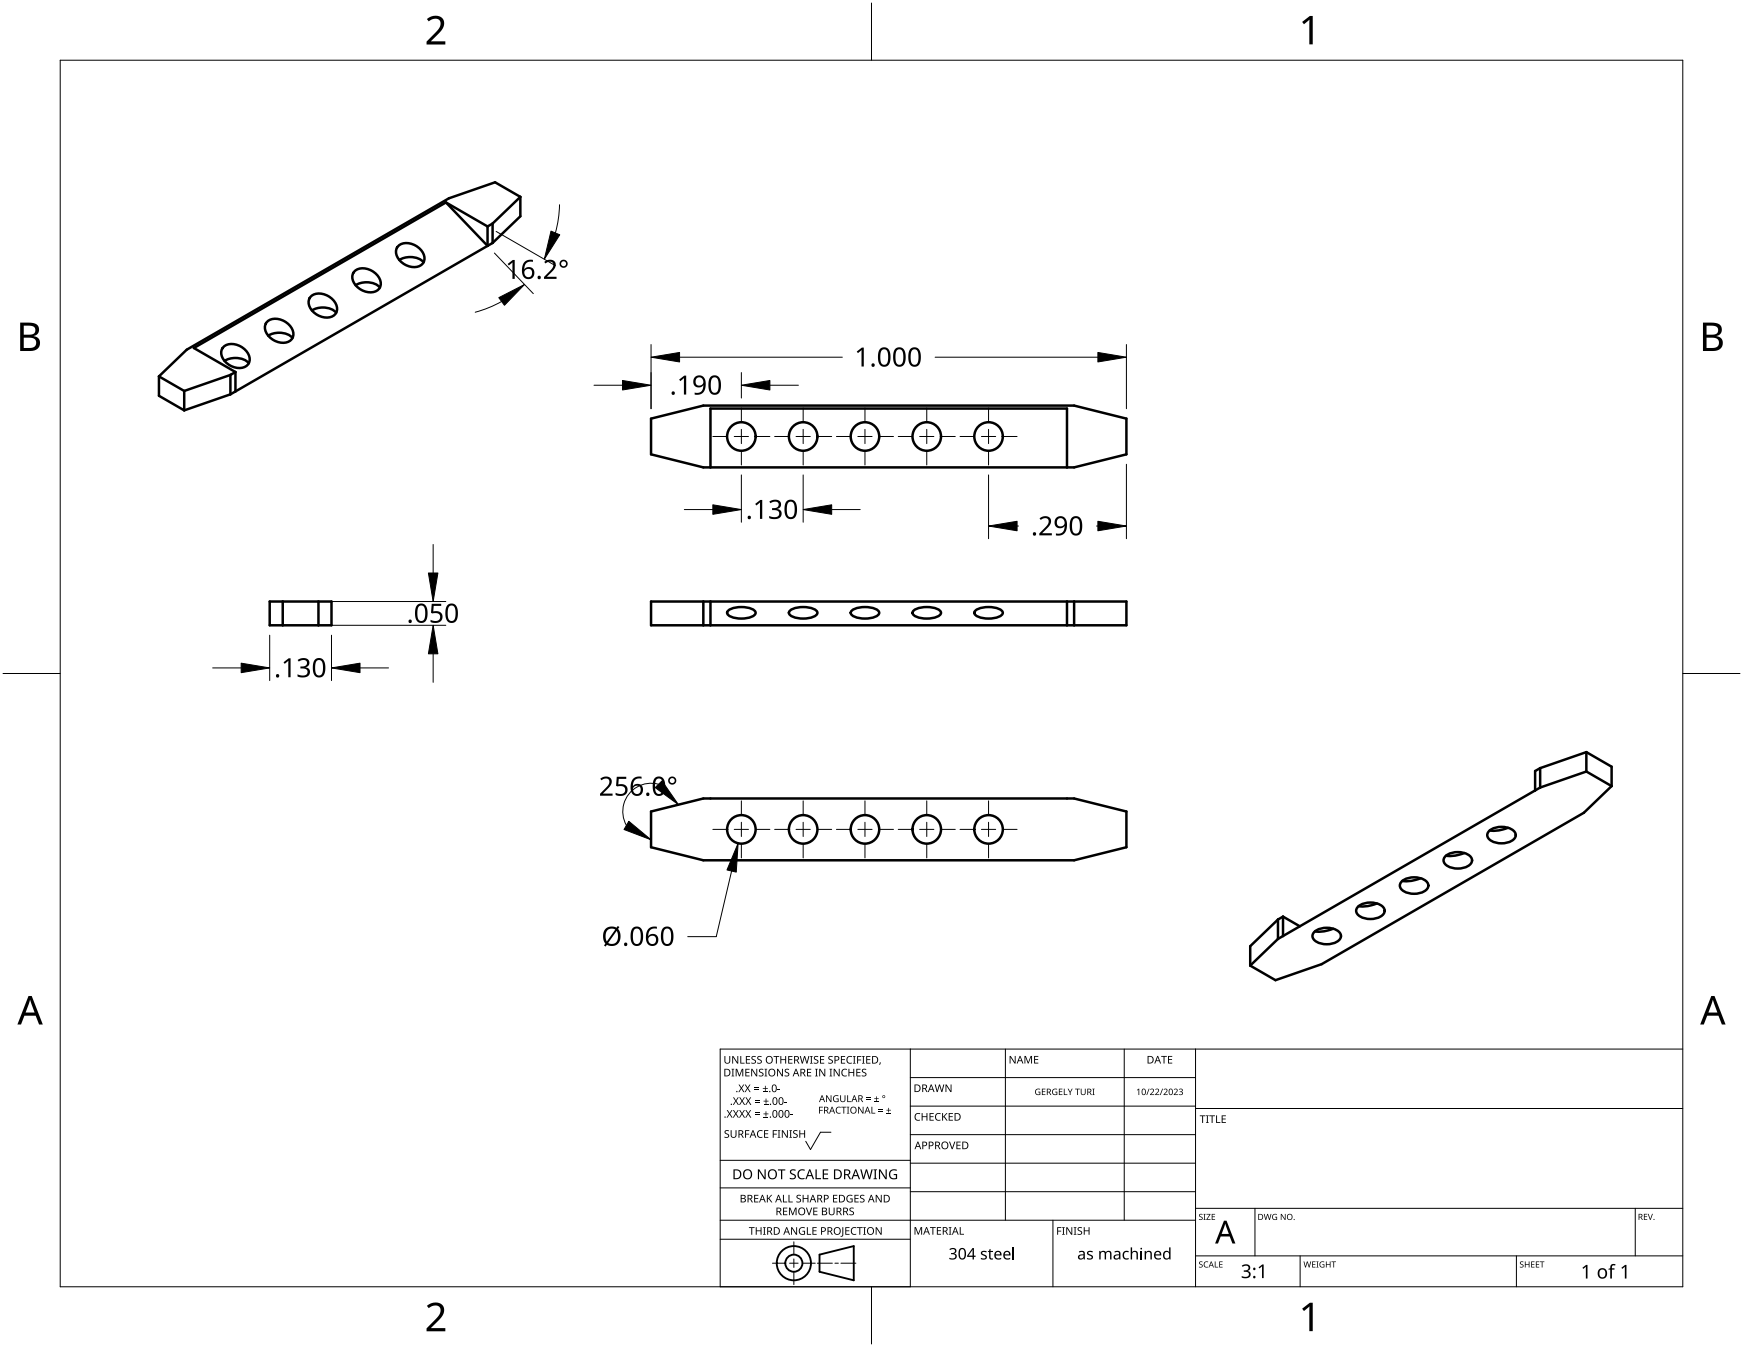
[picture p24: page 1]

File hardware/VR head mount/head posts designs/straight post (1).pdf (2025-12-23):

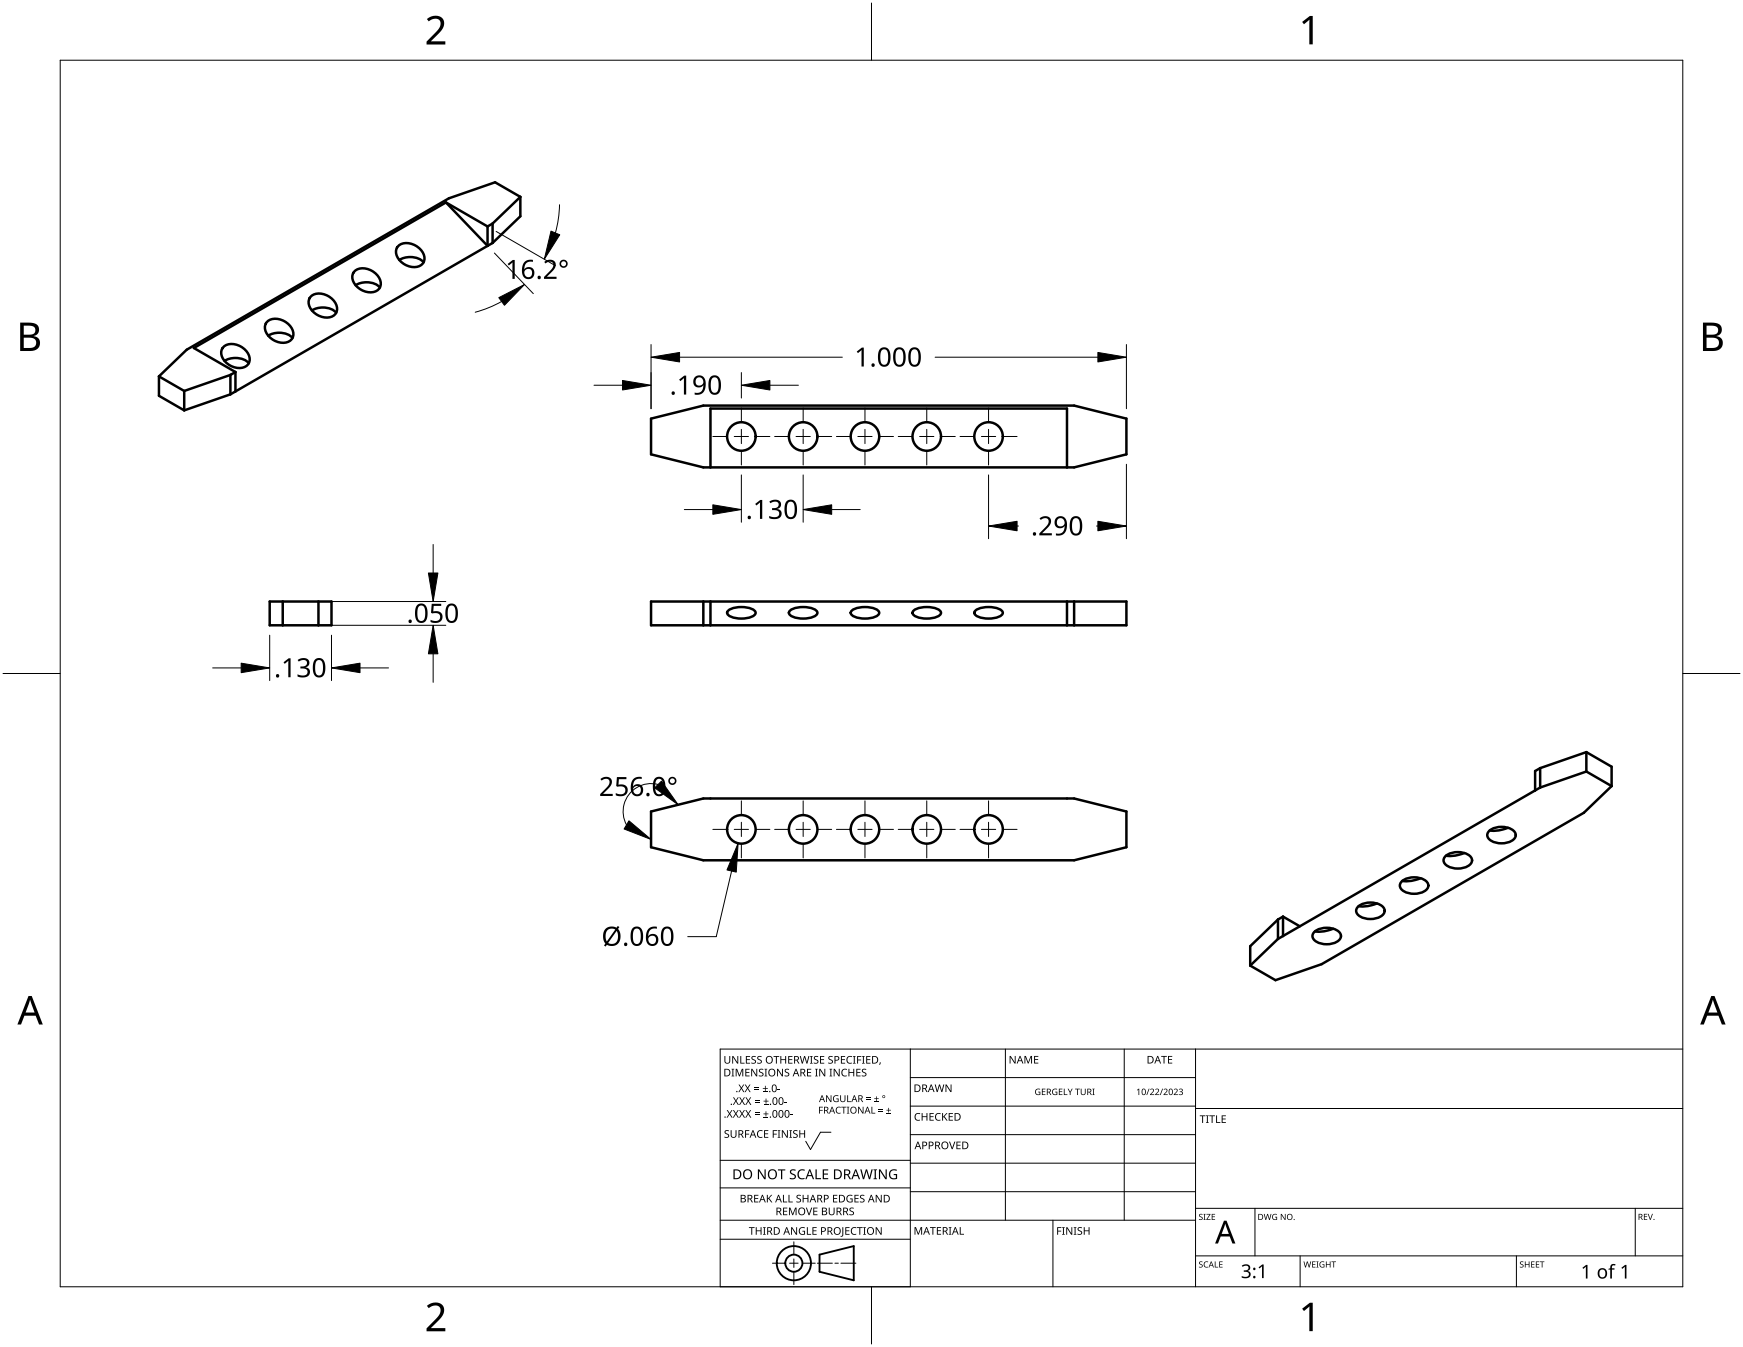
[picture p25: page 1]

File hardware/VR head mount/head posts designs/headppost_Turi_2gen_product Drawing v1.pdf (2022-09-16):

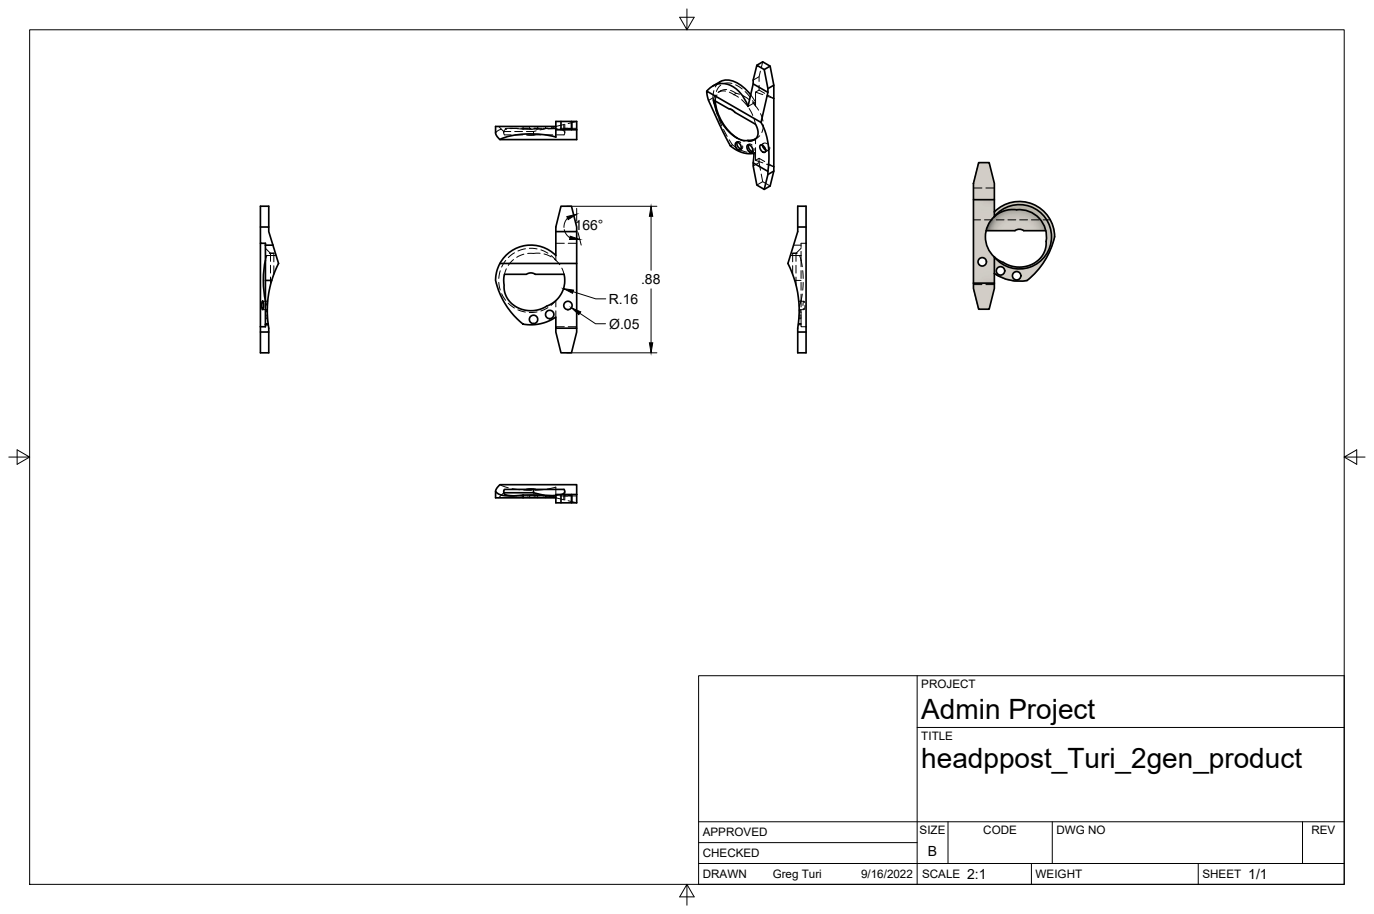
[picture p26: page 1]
SIZE; CODE; DWG NO; REV; Greg Turi; Admin Project

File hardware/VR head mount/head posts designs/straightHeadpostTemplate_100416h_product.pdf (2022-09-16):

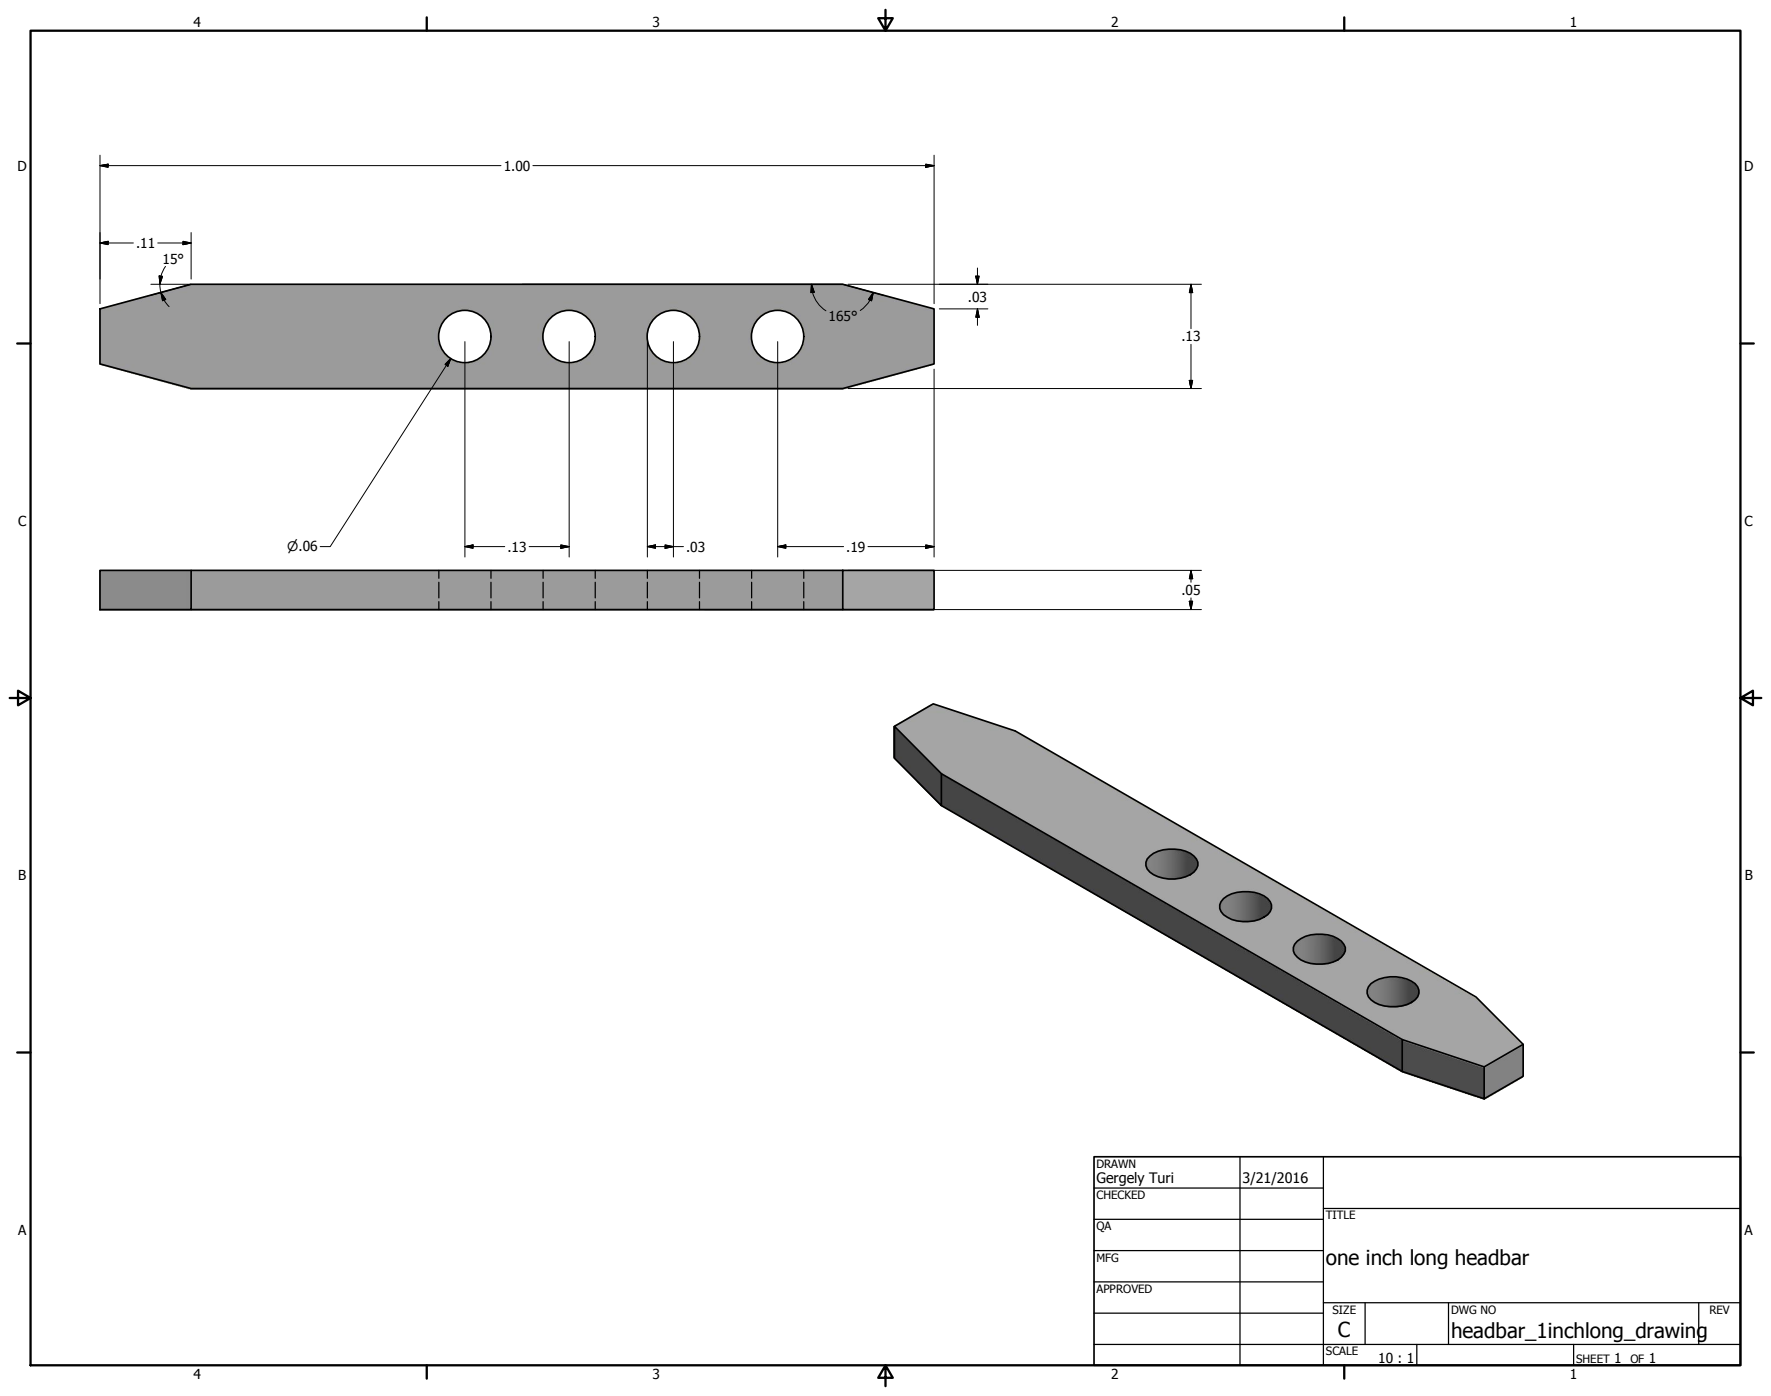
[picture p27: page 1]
SHEET 1 OF 1; DRAWN; CHECKED; MFG; APPROVED; Gergely Turi; DWG NO headbar_1inchlong_drawing; SIZE C; SCALE; REV

TITLE
one inch long headbar

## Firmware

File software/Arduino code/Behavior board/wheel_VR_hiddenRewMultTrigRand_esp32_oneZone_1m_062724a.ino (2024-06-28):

/*
  wheel_VR_hiddenRewMultTrigRand_esp32_1m_091722c.ino
  from: treadmill_hiddenRewardMultTrigRFIDrand_(date).ino
  Clay 2022

  Using on OpenMaze OMw small PCB
  for VR behavior.
  - Position input from rotary encoder ESP32 on Serial2
  - Solenoid valve control for liquid reward on ULN2803 (or H-bridge)
  - Lick detection with capacitive touch sensor (ESP32 or other)
  - Olfactory stim/airpuff via solenoid valve
  - Zero position on input from VR (via rotary ESP32)
  - Multiple reward position random option (isRandRew)
  - Operant/non on alternate laps option (altOpt)
  

*/


/// VARIABLES TO CHANGE EXPERIMENT PARAMS
String programName = "wheel_VR_hiddenRewMultTrigRand_esp32_1m_092422a";

int rewDur = 100;
int isESP = 1;  // 1 if you're detecting licks with ESP32 touch pins
int isButtonStart = 1;  // this means that prog doesn't print out position data until button is pressed
int isOperant = 1;  // animal has to lick to get reward
int altOpt = 0; // alternate operant on even laps? 
int maxNumZoneRew = 5;//5;
int rewTimeout = 500;//1000; //5000; // timeout for multiple reward licks within a single zone/epoch

int lickThresh = 120;//4;//50; //150; // 5*touch thresh value (for 5 read sum)

// reward vars
int numRew = 1; //8; // number of reward zones (if isRandRew=0, make equal to length rewPosArr) 
int rewWidth = 300;//200;//450;  // width of reward zone
int isRandRew = 0;
int rewPosArr[] = {1500}; //{1500};// {100, 500, 1000, 1500, 2000, 2500, 3000, 3500}; // specify exact positions if isRandRew=0
int rewZoneOptTime = 4000;  //2000; // ms after entering rewZone animal has the option to lick for rew
long interLickInt = 2;  // make really large if you want single lick choice (but might have to use 'long' var)

int trackLength = 2000;//1800;//0;
int startSession = 0;

// for velocity-based reward
int isVelRew = 0;   // reward if animal reaches a certain min velocity (in rotary clicks)
float velThresh = 20;  // for velRew
int velRewTimeout = 2000;

int evPos1 = 900; // olfactory stim params
int evWidth1 = 200;
int prevEv1 = 0;

// mult rew location defaults
int rewPosInds[] = {0, 1, 2, 3, 4, 5, 6, 7}; //,12}; // indices of reward zones (zero based)
int rewPosArrMaster[] = {40, 250, 500, 750, 1000, 1250, 1500, 1750}; //{100, 500, 1000, 1500, 2000, 2500, 3000, 3500}; //, 3600}; // possible start positions of reward zones
int numZones = 8; // the length of rewPosArrMaster

int rollOver = 0; // just to make tolerance for long belt (treadmill)

long rewZoneStartTime = 0;
int rewZone; // = 0;
int prevRewZone = 0;

int numZoneRew = 0;
int lastRewZone = 100;
int numRewZone = 0;

// sync pulse params
int syncDur = 500;  // duration of pulse
int syncIntv = 5000;  // interval of pulse train

////////////////PINS
// Pin numbers
int lickPin = 36;//2;//
//int spkrPin = 47;
int ledPin = 13;
int buttonPin1 = 15;
int trigPin = 2;//12;//26;  // pin for triggering nVista imaging (high during session if isButtonStart)
int syncPin = 33; // pin for nVista sync
int syncPin2 = 25;  // LED for video sync
int solPin1 = 14;//12; //5;
int solPin2 = 32; //6;

int touchPin = T0; // = pin 4, if using esp32 touch sensing

#define RXD2 16 // for Serial2 on ESP32
#define TXD2 17

/////////////////////

// times
long startTime = 0;
long endTime = 0;

//
int currPos = 0;
int prevPos = 0;
int dy = 0;
float vel = 0;

// rotary encoder serial input variables
String inputString = "";         // a string to hold incoming data
boolean stringComplete = false;  // whether the string is complete

int yInd = 0; // more encoder vars
int mInd = 0;
String dyStr = "";
String msStr = "";
long dt = 0;
long reTime = 0;
long prevReTime = 0;

long syncStartTime = 0; // sync vars
long prevSyncTime = 0;
int prevSync = 0;
long lastSyncTime = 0;

// initialize times and counts
int prevRew = 0;
long rewStartTime = 0;

// lick vars
int prevLick = 0;
long lickTime = 0;
long prevLickTime = 0;
int lickState = 0;
int lickStateArr[6];
int numReading = 0;
int lickStateSum = 0;
int justLicked = 0;  // for MPR

// esp32 lick vars
int touchVal = 0;

long buttonTime = 0;
long prevButtonTime = 0;

int isRewZone = 0;
int rewZoneSum = 0;

int lapNum = 0;

// SETUP ///////////////////
void setup()
{
  // set up pins
  pinMode(lickPin, INPUT);
  //pinMode(spkrPin, OUTPUT);
  pinMode(ledPin, OUTPUT);
  pinMode(solPin1, OUTPUT);
  pinMode(solPin2, OUTPUT);
  pinMode(buttonPin1, INPUT_PULLUP);
  pinMode(syncPin, OUTPUT);
  pinMode(trigPin, OUTPUT);
  pinMode(syncPin2, OUTPUT);

  //digitalWrite(solPin1, LOW);

  // Open serial communications (to computer)
  Serial.begin(115200);
  while (!Serial) {
    ; // wait for serial port to connect. 
  }

  // set the data rate for the rotary encoder port
  // NOTE: must match the rate of the rotary encoder ESP32
  Serial2.begin(115200, SERIAL_8N1, RXD2, TXD2); // Serial2 on ESP32
  inputString.reserve(200);
  //delay(1000);

  printHeader();

  if (!isESP) {
    lickThresh = 4;
  }

  randomSeed(analogRead(A4));

}  // end SETUP

// start LOOP  ///////////////////////////
void loop() // run over and over
{
  serialEvent1(); // look for input from PC/RasPi via rotary ESP32 (e.g. from Processing start to reprint header)
  
  // read rotary encoder input
  serialEvent2(); // reads movement and runs updatePosition

  // see if you need to turn off reward valve (for any given reward)
  if (prevRew == 1) {
    checkRewState();
  }

  checkLicks();

  //if (isButtonStart == 1) {
    checkButton();
  //}
  if (startSession == 1) {
    checkSyncState();
  }

}  // end LOOP


// SUBFUNCTIONS ////////////////////

// use rotary input to update position (and check if reward zone) every rotary read
void updatePosition() {
  //prevPos = currPos;
  
  // parse serial input from rotary encoder ESP32
  yInd = inputString.indexOf(',');
  dyStr = inputString.substring(0, yInd); //(yInd+4, mInd-3); //strtok(inputString, ","); //
  //    Serial.println(dyStr);
  dy = dyStr.toInt();
  mInd = inputString.indexOf(',', yInd);
  msStr = inputString.substring(mInd, inputString.length() - 1); //(mInd+8, inputString.length()-1);//strtok(NULL, ","); //
  reTime = msStr.toInt(); // rotary encoder arduino time
  dt = reTime - prevReTime;
  prevReTime = reTime;

  vel = dy; //float(dy)/float(dt)*1000;
  currPos = prevPos + dy;
  prevPos = currPos;

  // only print output and check reward zone after track calibrated and session started
  if (startSession == 1) {

    Serial.print("vel=" + String(vel) + ", ");
    Serial.println("currPos=" + String(currPos) + ", ms=" + String(millis()));

    // see if mouse is in any reward zone (but need to change so he can't go back through)
    rewZoneSum = 0;
    for (int i = 0; i < numRew; i++) { // check through all possible reward zones (nb. order not sorted)
      if (currPos >= rewPosArr[i] && currPos <= rewPosArr[i] + rewWidth) { // if currPos is in a rewZone
        rewZone = i; // number of curr rew zone in rewPosArr (nb. order not sorted)
        if (prevRewZone == 0 && rewZone != lastRewZone) { // if new entry into new zone (this prevents re-entry rewards)
          //rewZone = i;
          lastRewZone = i;
          numRewZone = numRewZone+1; // number/index of this reward zone along track this lap (nb. not ind in rewPosArr)
          rewZoneStartTime = millis();
          Serial.println("rewZone=" + String(numRewZone) + ", ms=" + String(rewZoneStartTime));
          //            isRewZone = 1;
          //            prevRewZone = 1;
          //            rewZoneSum = rewZoneSum +1;
          //break;
          
        }
        isRewZone = 1;
        prevRewZone = 1;
        rewZoneSum = rewZoneSum + 1;
      }
    }

    if (rewZoneSum == 0) {  // else if not in any reward zone
      isRewZone = 0;
      prevRewZone = 0;
      numZoneRew = 0;
    }

    if (isVelRew == 0 && isRewZone == 1) {    // for non-operant rewards in rewZone entry
      if (isOperant == 0 && prevRew == 0 && millis() - rewStartTime > rewTimeout && numZoneRew < maxNumZoneRew) {
        prevRew = 1;
        numZoneRew = numZoneRew + 1;
        giveReward();
      }
      //digitalWrite(ledPin, HIGH); // to turn on LED while in rew zone
    }  // end IF in rewZone
    else {
      //digitalWrite(ledPin, LOW);
      isRewZone = 0; // this turns off rewZone if isVelRew
    }

    // if pos is more than estimate of track length, start new lap
    if (currPos >= trackLength + rollOver) {
      lapReset();
    }

    // if isVelRew and vel is high enough, give reward
    if (isVelRew == 1 && vel > velThresh && millis() - rewStartTime > velRewTimeout) {
      giveReward();
      prevRew = 1;
    }

    /////////////olf stim NEW
//    if (currPos >= evPos1 && currPos < evPos1 + evWidth1) {
//      if (prevEv1 == 0) {
//        digitalWrite(solPin2, HIGH);
//        Serial.print("olfOn, ms=");
//        Serial.println(millis());
//        prevEv1 = 1;
//      }
//    }
//    else {
//      if (prevEv1 == 1) {
//        digitalWrite(solPin2, LOW);
//        Serial.print("olfOff, ms=");
//        Serial.println(millis());
//        prevEv1 = 0;
//      }
//    }

    /// ADD NEW POSITION EVENTS HERE
    /// e.g.  if (currPos >= eventPos1 && currPos < eventPos1+zoneWidth) {tone(pin, freq);} else {noTone(pin);}
    ///
    ///

  }
}

////////////////////////////////////////////
////////basic event state check functions
// reward functions
void giveReward() {
  rewStartTime = millis();
  digitalWrite(solPin1, HIGH);
  Serial.print("REWARD, ms=");
  Serial.println(rewStartTime);
  //delay(500);
}

void checkRewState() {
  if (prevRew == 1 && millis() - rewStartTime >= rewDur) {
    digitalWrite(solPin1, LOW);
    prevRew = 0;
  }
}

///////////////////////
void checkButton() { // for button start
  if (digitalRead(buttonPin1) == 0) {
    if (millis() - prevButtonTime > 2000) {
        prevButtonTime = millis();
        Serial.print("exp");
        giveReward();
        prevRew = 1;
      if (startSession == 0) {
        startSession = 1;
        startTime = millis();
        digitalWrite(trigPin, HIGH); // trig stays HIGH whole session after button start
        Serial.print("START SESSION button, ms = ");
        Serial.println(startTime);
        Serial.print("trigTime, ms=");
        Serial.println(startTime);
        prevButtonTime = startTime;

      }
      else {
        startSession = 0;
        endTime = millis();
        digitalWrite(trigPin, LOW);
        digitalWrite(syncPin, LOW);
        digitalWrite(syncPin2, LOW);
        Serial.print("END session button, ms=");
        Serial.println(endTime);
        prevButtonTime = endTime;
      }
    }
  }
}

////////////////////////
void checkSyncState() {
  if (prevSync == 1 && millis() - syncStartTime >= syncDur) {
    digitalWrite(syncPin, LOW);
    digitalWrite(syncPin2, LOW);
    prevSync = 0;
  }
  else if (millis() - lastSyncTime >= syncIntv) {
    digitalWrite(syncPin, HIGH);
    digitalWrite(syncPin2, HIGH);
    syncStartTime = millis();
    Serial.print("syncOut, ms = ");
    Serial.println(syncStartTime);
    lastSyncTime = syncStartTime;
    prevSync = 1;
  }
}
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

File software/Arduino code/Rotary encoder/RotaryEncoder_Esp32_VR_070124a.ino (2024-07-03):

/*
 * This is from a basic example from the
 * AiEsp32RotaryEncoder library
 * "TheShortestExample"
 * Clay modified for treadmill use by
 * making output in JSON like previous
 * HCTL rotary encoder.
 * Also made hack for rollover.
 * 
 * 081222
 * Changing for VR to output simple (non JSON)
 * 
 */


#include "AiEsp32RotaryEncoder.h"
//#include <ArduinoJson.h>
/////////////////////
#define RXD2 16 // for Serial2 on ESP32
#define TXD2 17
/////////////////////
#define ROTARY_ENCODER_A_PIN 27
#define ROTARY_ENCODER_B_PIN 26
#define ROTARY_ENCODER_BUTTON_PIN 25
#define ROTARY_ENCODER_STEPS 4
AiEsp32RotaryEncoder rotaryEncoder = AiEsp32RotaryEncoder(ROTARY_ENCODER_A_PIN, ROTARY_ENCODER_B_PIN, ROTARY_ENCODER_BUTTON_PIN, -1, ROTARY_ENCODER_STEPS);

/////////////////////////////
//StaticJsonBuffer<200> jsonBuffer;
//JsonObject& message = jsonBuffer.createObject();
//JsonObject& value = message.createNestedObject("position");;
//////////////////////////////

int printInt = 30; // print rotary output every Xms

int dy = 0;
int prevDy = 0;
int val = 0;
int prevVal = 0;
long currT = 0;

String inputString = "";         // a string to hold incoming data
boolean stringComplete = false;  // whether the string is complete

///////////////////////////
void rotary_onButtonClick()
{
    Serial.println("button pressed");
}

///////////////////////////
void setup()
{
    Serial.begin(115200);
    Serial2.begin(115200, SERIAL_8N1, RXD2, TXD2); // Serial2 on ESP32
    
    rotaryEncoder.begin();
    rotaryEncoder.setup(
        [] { rotaryEncoder.readEncoder_ISR(); },
        [] { rotary_onButtonClick(); });
    rotaryEncoder.setBoundaries(0, 1000, true); //minValue, maxValue, circleValues true|false (when max go to min and vice versa)
    rotaryEncoder.setAcceleration(0);

//    value["dy"] = 0;
//    message["millis"] = 0;
}
///////////////////////////
void loop()
{
    if (rotaryEncoder.encoderChanged())
    {
        val = rotaryEncoder.readEncoder();
        //Serial.println(val);
//        prevVal = val;

        currT = millis();
        
        dy = val-prevVal;

        if (dy>=900 || dy<=-900) { // build in catch for rollover (ins prev good val)
          dy = prevDy;
        }

//        // print JSON to main Serial/USB
//        value["dy"]=dy;
//        message["millis"]=currT;
//        message.printTo(Serial);
//        Serial.println();

        Serial.print(dy); Serial.print(","); Serial.println(currT); // or simple to USB

        // print simple to esp32 Serial2
        Serial2.print(dy); Serial2.print(","); Serial2.println(currT);
        
        prevVal = val;
        prevDy = dy;
    }
//    else {
//      Serial.println(prevVal);
//    }
    delay(printInt);

    serialEvent1();
}
/////////////////////////////
// Read data from RasPi VR (Serial2) to reset behav arduino pos
void serialEvent1() {
  while (Serial2.available()) {
    //Serial.println("Reading...");
    // get the new byte:
    char inChar = (char)Serial2.read(); // read RasPi serial
    //Serial.println(inChar);
    // add it to the inputString:
    inputString += inChar;
    // if the incoming character is a newline, set a flag
    // so the main loop can do something about it:
    if (inChar == '\n') {
      stringComplete = true;
      Serial.print(inputString); // output to behav arduino/esp32

//      // reset arduino pos if '0' from VR RasPi
//      if (inputString.equals("0")) {
//        Serial.println("VR reset");
//        prevPos = 0;
//        prevRew = 0;  // reset reward
//      }
      
      // clear the string:
      inputString = "";
      stringComplete = false;

    }
  }
}

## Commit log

2020-09-28 componenst for the old clamp
    [BASEPLATE.ipt, CLAMP_BAR.ipt, HEADPOST_BAR_W_SLOT_ADJUST.ipt, HEADPOST_BAR_W_SLOT_FIXED_POS.ipt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]
2020-10-23 position controller data added
    [position_controller.csv, position_controller.kicad_pcb, position_controller.sch, quadrature_calc.ods]
2021-03-12 Add files via upload
    This is the prototype of the virtual corridor
2021-05-12 Add files via upload
    #1) Generate drop menu for combination
    #2) Set combination pattern change Simultaneously
    #3) Add background timer/clean comb list function using thread
    #4) Finish rest 2 combination
2021-05-13 Add files via upload
    #1) Add path canvas
    #2) Add buffer to speed up
    #3) Add read file function to image folder
    #4) Give history, output file
    # --- For Image input ---
    # --- size should be equal or above 5cm x 5cm, file type should be .jpg
2021-05-19 Add files via upload
    First Prototype for Corridor. Bypass bug but need to fix
2021-05-20 Add files via upload
    First System Prototype
2021-06-17 Add files via upload
    re-design of Encoder using STM32
2021-07-08 ESP32_rotary_encoder(delay 25)
2021-07-22 Add files via upload
    ESP32 bluetooth
2022-01-14 ESP32 rotary encoder example
2022-01-14 Working version of Bluetooth/Wired
2022-09-07 Create Final1 v1.stl
    [Final1 v1.stl]
2022-09-07 Create v1 v9.step
    [v1 v9.step]
2022-09-07 3d model update
    [Final1 v1.step, v1 v9.step, v2 v10.step, v3 v3.step]
2022-09-14 adding to VR mount
2022-09-14 refactoring, adding new structure
    [BASEPLATE.ipt, CLAMP_BAR.ipt, Final1 v1.step, HEADPOST_BAR_W_SLOT_ADJUST.ipt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]
2022-09-16 new stuff
    [position_controller.csv, position_controller.kicad_pcb, position_controller.sch, quadrature_calc.ods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]
2022-09-16 changes in lickport assembly
2022-09-16 adding PCBs
    [OMw small 032222a - Bottom Copper (Paste).gbr, OMw small 032222a - Bottom Copper.gbr, OMw small 032222a - Bottom Solder Mask.gbr, OMw small 032222a - Drill Dat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]
2022-09-20 Folder
    vr mount folder does not work, and I was not allow to create a new folder outside the existing one so I organize and put everything in the vr head mount folder instead
    [Final1 v1.step, Headpost Clamp.step, Laser Cut Part.step, Screen Assemblies.step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]
2022-09-21 Create Headpost and Clamp.png
2022-09-23 Clay's branch
    [Headpost Clamp.step, Laser Cut Part.step, OMw small 032222a - Bottom Copper (Paste).gbr, OMw small 032222a - Bottom Copper.gbr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]
2022-09-23 temp after trying to merge Clay's branch
    [Headpost Clamp.step, Laser Cut Part.step, OMw small 032222a - Bottom Copper (Paste).gbr, OMw small 032222a - Bottom Copper.gbr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]
2022-09-23 adding two more subfolder for arduino code
2022-09-26 2D and 3D of wheel and screen
    [Wheel and Sceen.step]
2022-09-26 adding capacitive sensor part num
2022-09-26 modifying a few descriptions.
    [Wheel and Sceen.step]
2022-09-26 Adding rotary encoder ESP32 arduino code.
2022-09-26 Adding behavior ESP32 example code.
2022-09-27 adding lik port folder and some other changes
    [runningWheel_6inCyl_sideMount_JoVE_091422a.dxf]
2022-09-28 refactoring, removing VR electronics/ESP32 files
    [position_controller.csv, position_controller.kicad_pcb, position_controller.sch, quadrature_calc.ods]
2022-09-30 New gonio/headfix mount plate design.
2022-10-03 New GUI file with frame labels
    Rename to HallPassVR_GUI.py and replace old version
2022-10-04 Annotated wheel laser cut file
2022-10-04 Slight change to annotated wheel laser cut file
2024-07-03 clay updated arduino code
2025-12-23 Add files via upload
    Straight headpost designs with a 45 angle so it accommodates the arch of the head easier.
    [straight headpost.step, straight post0.step]
